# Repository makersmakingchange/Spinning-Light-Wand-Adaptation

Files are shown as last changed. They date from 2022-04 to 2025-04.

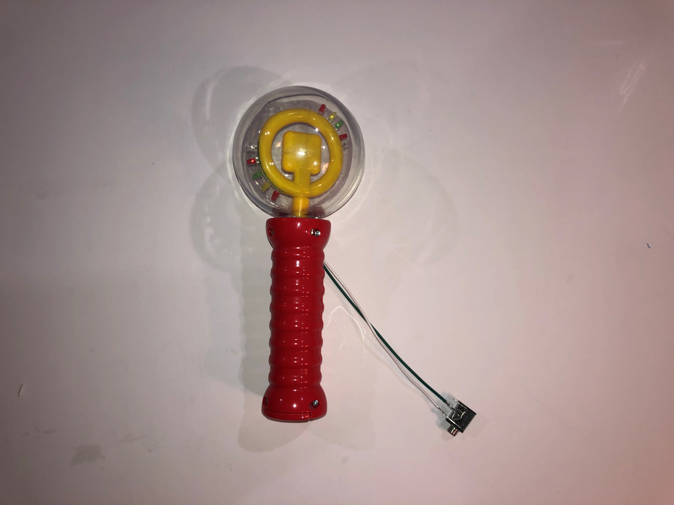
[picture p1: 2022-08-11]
Photos/solder the monojack.jpg

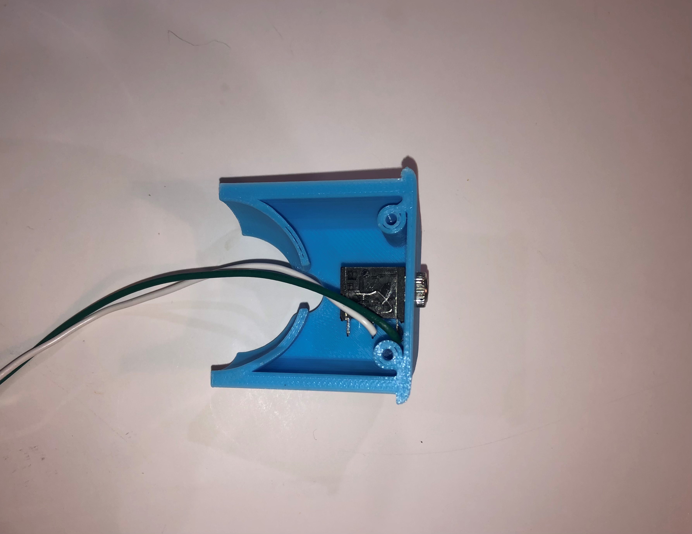
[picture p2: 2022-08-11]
Photos/mono jack.jpg

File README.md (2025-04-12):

# Spinning Light Wand Adaptation
The Spinning Light Wand Adaptation comprises instructions and files to adapt a commercially available Spinning Light Wand toy for use with an assistive switch. The toy is modified so that it has a 3.5 mm jack in place of the button. When a standard assistive switch with a 3.5 mm mono jack is attached and activated, the toy will activate. The toy is mounted into a 3D printed base that keeps the toy upright and houses the input jack. 

A switch-adapted Spinning Light Wand mounted in a blue 3d-printed base.

## More info at
- Makers Making Change Project Page: https://makersmakingchange.com/project/spinning-light-wand-toy-adaptation/
- Vancouver Hack Space Forum Thread: https://talk.vanhack.ca/t/adapting-toy-wands-for-mmc

## Getting Started

### 1. Order the Off-The-Shelf Components

The [Bill of Materials](/Documentation/Working_Documents/Spinning_Light_Wand_BOM_V1.1.xlsx) lists all of the parts and components required to adapt the Spinning Light Wand. The toy is typically available at Walmart stores.

### 2. Print the 3D Printable components
Print the components. All of the files and individual print files can be in the [Build_Files](Build_Files) folder.

### 3. Assembly
Reference the [Assembly Guide v1.0](/Documentation/Spinning_Light_Wand_Assembly_Guide_V1.0.pdf) or [Assembly Guide v1.1](/Documentation/Spinning_Light_Wand_Assembly_Guide_V1.1.pdf) for the tools and steps required to build each portion.

## Files
### Documentation
| Document             | Version | Link |
|----------------------|---------|------|
| Design Rationale     | 1.1     | [Spinning_Light_WandDesign_Rationale](/Documentation/Spinning_Light_Wand_Design_Rationale.pdf)     |
| Bill of Materials    | 1.1     | [Spinning_Light_Wand_Bill_of_Materials](/Documentation/Working_Documents/Spinning_Light_Wand_BOM_V1.1.xlsx)     |
| 3D Printing Guide    | 1.1     | [Spinning_Light_Wand_3D_Printing_Guide](/Documentation/Spinning_Light_Wand_3D_Printing_Guide.pdf)     |
| Assembly Guide       | 1.0     | [Spinning_Light_Wand_Assembly_Guide](/Documentation/Spinning_Light_Wand_Assembly_Guide_V1.0.pdf)     |
| Assembly Guide       | 1.1     | [Spinning_Light_Wand_Assembly_Guide](/Documentation/Spinning_Light_Wand_Assembly_Guide_V1.1.pdf)     |
| Maker Checklist      | 1.1     | [Spinning_Light_Wand_Maker_Checklist](/Documentation/Spinning_Light_Wand_Checklist.pdf)     |
| User Guide           | 1.0     | [Spinning_Light_Wand_User_Guide](/Documentation/Spinning_Light_Wand_User_Guide_V1.0.pdf)    |
| User Guide           | 1.1     | [Spinning_Light_Wand_User_Guide](/Documentation/Spinning_Light_Wand_User_Guide_V1.1.pdf)    |
| Changelog            | 1.1     | [Spinning_Light_Wand_Changelog](/Documentation/Spinning_Light_Wand_Changelog.pdf)     |

### Design Files
- [CAD Files](/Design_Files)

### Build Files
 - [3D Printing Files](/Build_Files)

## Attribution
This adaptation was designed by Mimi Xia of the [Makers Making Change Vancouver Chapter](https://vanhack.ca/wp/makers-making-change-vancouver-chapter/). 

3D Printed Wand Base v1.0 designed by Mimi Xia.

3D Printed Wand Base v1.1 designed by Jake McIvor – Makers Making Change.

Neil Squire / Makers Making Change assisted with the creation of the documentation.

## License
Everything needed or used to design, make, test, or prepare the Spinning Light Wand Adaptation is licensed under the CERN 2.0 Permissive license https://ohwr.org/project/cernohl/wikis/Documents/CERN-OHL-version-2 (CERN-OHL-P) .

Accompanying material such as instruction manuals, videos, and other copyrightable works that are useful but not necessary to design, make, test, or prepare the Spinning Light Wand Adaptation are published under a Creative Commons Attribution-NonCommercial-ShareAlike 4.0 license https://creativecommons.org/licenses/by-nc-sa/4.0/ (CC BY-NC-SA 4.0)

----

<!-- ABOUT MMC START -->
## About Makers Making Change
[Makers Making Change Logo](https://www.makersmakingchange.com/)

Makers Making Change is a program of [Neil Squire](https://www.neilsquire.ca/), a Canadian non-profit that uses technology, knowledge, and passion to empower people with disabilities.

Makers Making Change leverages the capacity of community based Makers, Disability Professionals and Volunteers to develop and deliver affordable Open Source Assistive Technologies.

 - Website: [www.MakersMakingChange.com](https://www.makersmakingchange.com/)
 - GitHub: [makersmakingchange](https://github.com/makersmakingchange)
 - Bluesky: [@makersmakingchange.bsky.social](https://bsky.app/profile/makersmakingchange.bsky.social)
 - Instagram: [@makersmakingchange](https://www.instagram.com/makersmakingchange)
 - Facebook: [makersmakechange](https://www.facebook.com/makersmakechange)
 - LinkedIn: [Neil Squire Society](https://www.linkedin.com/company/neil-squire-society/)
 - Thingiverse: [makersmakingchange](https://www.thingiverse.com/makersmakingchange/about)
 - Printables: [MakersMakingChange](https://www.printables.com/@MakersMakingChange)

### Contact Us
For technical questions, to get involved, or to share your experience we encourage you to [visit our website](https://www.makersmakingchange.com/) or [contact us](https://www.makersmakingchange.com/s/contact).
<!-- ABOUT MMC END -->

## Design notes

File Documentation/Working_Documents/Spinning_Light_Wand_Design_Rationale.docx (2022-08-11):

# Introduction

The toy should be activatable by connecting a standard assistive switch equipped with a 3.5 mm mono plug. This adaptation is intended for users that may have difficulty holding the toy and/or activating the small button independently.

# Requirements

## Goals

G01 | Make the toy more accessible by adding the ability to use an assistive switch.

## Functional Requirements

F01 | Must have a female 3.5 mm jack connected such that when tip and sleeve contacts are closed the toy activates.

## Non-functional Requirement

NF01

## Constraints

C01 | Adaptation should be suitable for a volunteer maker to complete.
C02 | Adaptation should require simple hand tools; screwdrivers, soldering iron

# Ideation

This toy has also been switch adapted by using a battery interrupter and using tape or a strap to fix the built-in button in the on position. A custom 3d printed collar could also be used to keep the built-in button depressed. This requires no permanent modification to the toy.

## Possible Alternatives

The following toys are a similar style but may have a different size or wiring.

### Rhode Island Novelty Light-up Magic Ball Wand, One Piece

- https://www.amazon.ca/Rhode-Island-Novelty-Magic-Flashing/dp/B009A6PIVG
- $ 16 CAD

### ArtCreativity Light up Orbiter Spinning Wand | 7â€� LED Electronic Spin Toy for Kids with Batteries Included | Great Gift Idea for Boys Girls Toddlers | Fun Birthday Party Favor/ Carnival Prize

- https://www.amazon.ca/ArtCreativity-Spinning-Electronic-Batteries-Included/dp/B07D7GQFMZ
- $20 CAD

### ArtCreativity 7.5 Inch Light Up Magic Ball Toy Wand for Kids - Flashing LED Wand for Boys and Girls - Thrilling Spinning Light Show - Batteries Included - Fun Gift or Birthday Party Favor

- https://www.amazon.ca/ArtCreativity-Inch-Light-Magic-Ball/dp/B07RG7DDW6
- $32 CAD

### Spinning Light-Up Wand for Kids in Gift Box, Rotating LED Toy Wand for Boys and Girls, Magic Princess Sensory Toys for Autistic Children, Best Birthday Gift for Kids 3, 4, 5, 6, 7

- https://www.amazon.ca/Spinning-Light-Up-Rotating-Princess-Autistic/dp/B082VFSJZP
- $43 CAD

# Prototyping

Several versions of the base were 3D printed and iterations and improvements were made accordingly. The 3D printed wand stand v1.0 was strudy but overall changes were made to decrease the print time of the device, as well as eliminate the need for supports. Some people suggested that it is rather difficult to get all of the supports off.

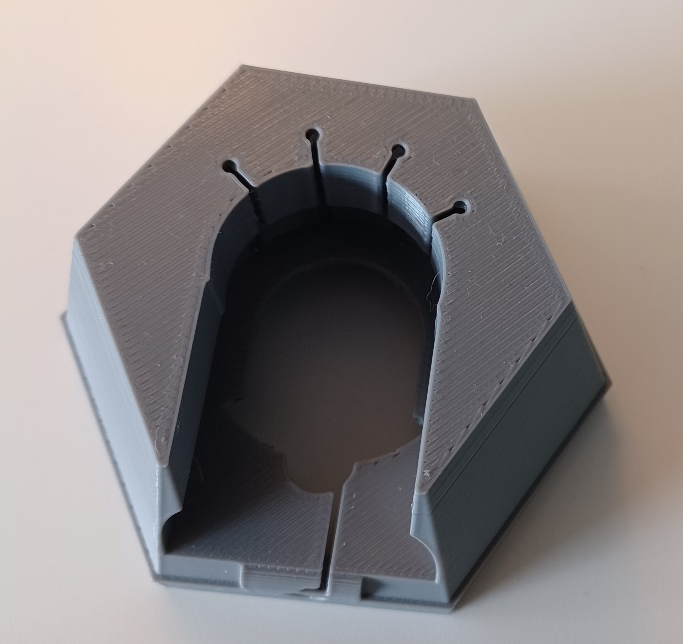
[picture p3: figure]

The Spinning Wand 3D Printed Stand v1.1 was developed as it requires no print supports, and has a quicker print time. Between iterations of this version of the wand stand, the following changes were made:

- Optimizing the hole in the base so that the battery cover could be removed in the event that the batteries need to be changed.
- Optimizing the clearance between the two 3D printed pieces so they were easy to slide together.

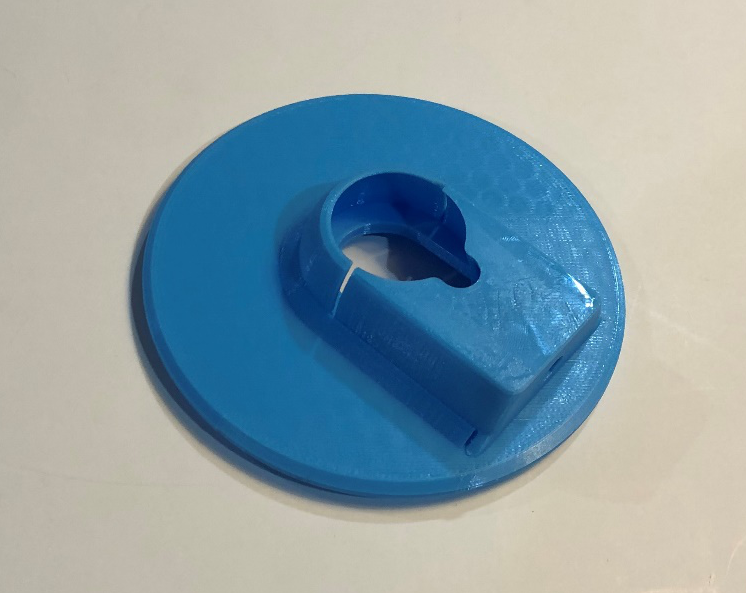
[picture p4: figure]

# Testing

The adapted toy has been tested by plugging in a switch into the 3.5mm jack located in the 3D printed base.

# Detailed Design – V1.1

## Spinning Light Wand Toy

The spinning wand toy used for this toy adaption was purchased at Walmart for $5.

- SKU 6000201173988
- https://www.walmart.ca/en/ip/spinning-light-wand-yellowblue/6000201173987

## 3D Printed Base

The 3D printed base was optimized to significantly reduce the print time, as well as eliminate the need for printing with supports. The supports on the first version of the device could be very challenging to remove, so there was a need to redesign the base. This was achieved by printing the base in 2 parts. As shown below, the smaller piece slides into the base to enclose the wand base between them. The mono jack sits in the circular hole. There are two small screw holes in each piece that align hold the two halves together. The bell-shaped hole in the 3D printed base is used to open the battery compartment on the wand without having to disassemble the 3D printed base.

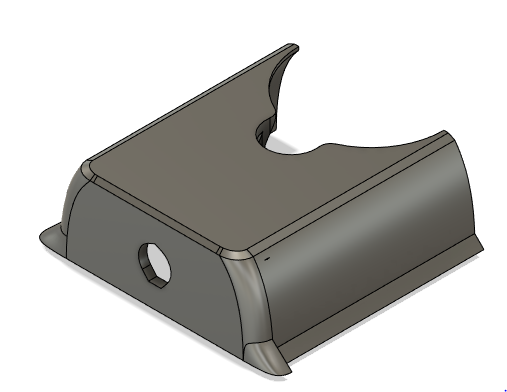
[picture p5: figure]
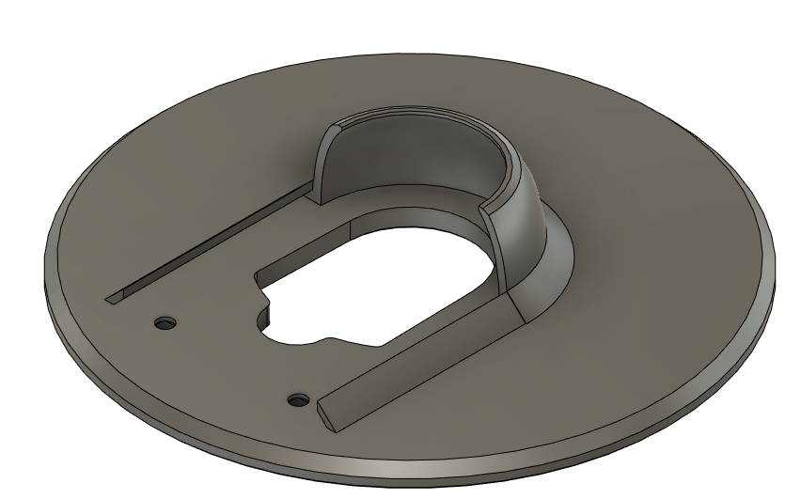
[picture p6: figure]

# Opportunities for Improvement

- Investigate options for putting external switch jack in parallel with built-in switch so that toy can be activated using either option
- The toy still slightly vibrates even with the non-slip circles. Further improvements are required to prevent the toy from moving.

© 2022 by Neil Squire / Makers Making Change. This work is licensed under the CC BY NC SA 4.0 License: http://creativecommons.org/licenses/by-nc-sa/4.0 Files available at https://makersmakingchange.com/project/spinning-light-wand-toy-adaptation/ Page 1 of 1

V1.1 | JUNE 2022 Spinning Light Wand Toy Adaptation Design Rationale

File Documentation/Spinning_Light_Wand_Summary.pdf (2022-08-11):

V1.1 | JUNE 2022

## Spinning Light Wand Toy Adaptation

## SUMMARY

© 2022 by Mimi Xia.
This work is licensed under the CC BY NC SA 4.0 License: http://creativecommons.org/licenses/by-nc-sa/4.0
Files available at https://makersmakingchange.com/project/spinning-light-wand-toy-adaptation/ (https://makersmakingchange.com/?post_type=project&p=14500&preview=true) | Page 1 of

### Title

Spinning Light Wand Toy Adaptation

### Subtitle

A switch adapted toy with spinning lights.

### Overview

The Spinning Light Wand Adaptation comprises instructions and files to adapt a commercially available Spinning Light Wand toy for use with an assistive switch. The toy is modified so that it has a 3.5 mm jack in place of the button.

### Usage

Connect an assistive switch with a 3.5 mm mono plug to the 3.5 mm mono jack on the base of the adapted toy. When the assistive switch is activated, the lights will turn on and spin within the plastic globe. The spinning wand stands in a 3D printed base. There are two versions of this base available for request: v1.0, and v1.1. Please specify to the maker which version you would like.

Cost
The cost of materials for this project is approximately $10-$15 CAD. This does not include the cost of component shipping.

Build Instructions
The necessary files and information required to switch adapt the toy switch are available in the linked GitHub repository or via the downloadable Zip file. The build consists of a commercially available toy, some 3D printed components, and some electronic components. Refer to the Spinning Light Wand Adaptation Assembly Guide.

Skills Required
- 3D Printing
- Soldering
- Mechanics

Time Required
Version 1.1:
- 3D Printing: ~3 hr
- Assembly: ~1 hr

Version 1.0:

- 3D Printing: ~6 hr

## SUMMARY

Files available at https://makersmakingchange.com/project/spinning-light-wand-toy-adaptation/ (https://makersmakingchange.com/?post_type=project&p=14500&preview=true) | Page 2 of
- Assembly: ~1 hr

Tools/Materials
Version 1.1:
- #0 Phillips Screwdriver
- #0 Robertson Screwdriver (depending on which screws you got)
- Soldering Iron & Solder
- Hot Glue Gun & Hot Glue sticks

Version 1.0:

- #0 Phillips Screwdriver
- Flat head screwdriver
- Soldering Iron & Solder
- Hot Glue Gun & Hot Glue sticks
- Super Glue

Components
Refer to the Bill of Materials.

Version 1.1:

- 1x Spinning Light Wand Toy
- 1x 3.5 m Mono Jack
- 2x 30cm pieces of wire
- 2x #4 1/2" screws
- 4x Nonslip Circles

Version 1.0:

- 1x Spinning Light Wand Toy
- 1x 3.5 m Mono Jack
- 2x 20cm pieces of wire

3D Printing
Refer to the Spinning Light Wand Adaptation 3D Printing Guide.

Version 1.1:

- 1x Wand Base
- 1x Jack Cover

Version 1.0:

## SUMMARY

Files available at https://makersmakingchange.com/project/spinning-light-wand-toy-adaptation/ (https://makersmakingchange.com/?post_type=project&p=14500&preview=true) | Page 3 of
- 1x Wand Base
- 1x Bottom Cover

### Attribution

This adaptation was designed by Mimi Xia of the [Makers Making Change Vancouver Chapter] (https://vanhack.ca/wp/makers-making-change-vancouver-chapter/) under the CC BY-SA 4.0 license.

3D Printed Wand Base v1.0 designed by Mimi Xia under the CC BY-SA 4.0 license.

3D Printed Wand Base v1.1 designed by Jake McIvor – Makers Making Change under the CC BY-SA 4.0 license.

Neil Squire / Makers Making Change assisted with the creation of the documentation that is under the CC BY-SA 4.0 license.

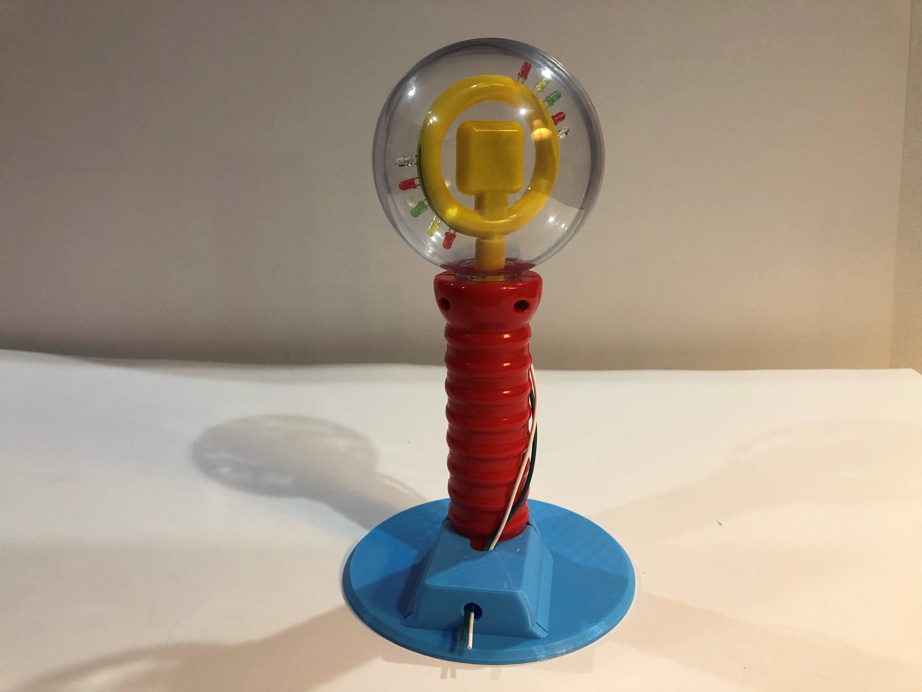
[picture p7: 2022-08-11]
Photos/feed wires through base.jpg

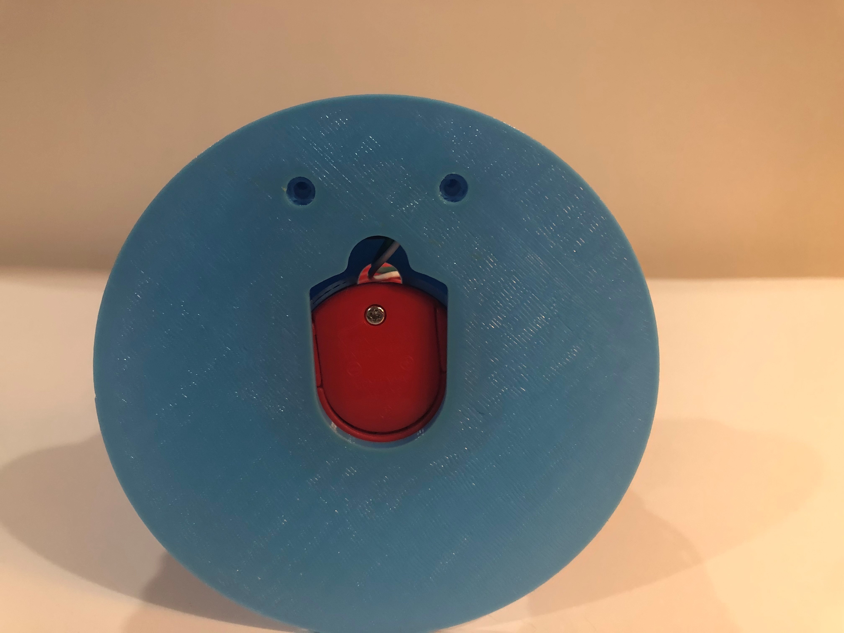
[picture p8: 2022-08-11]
Photos/battery cover.jpg

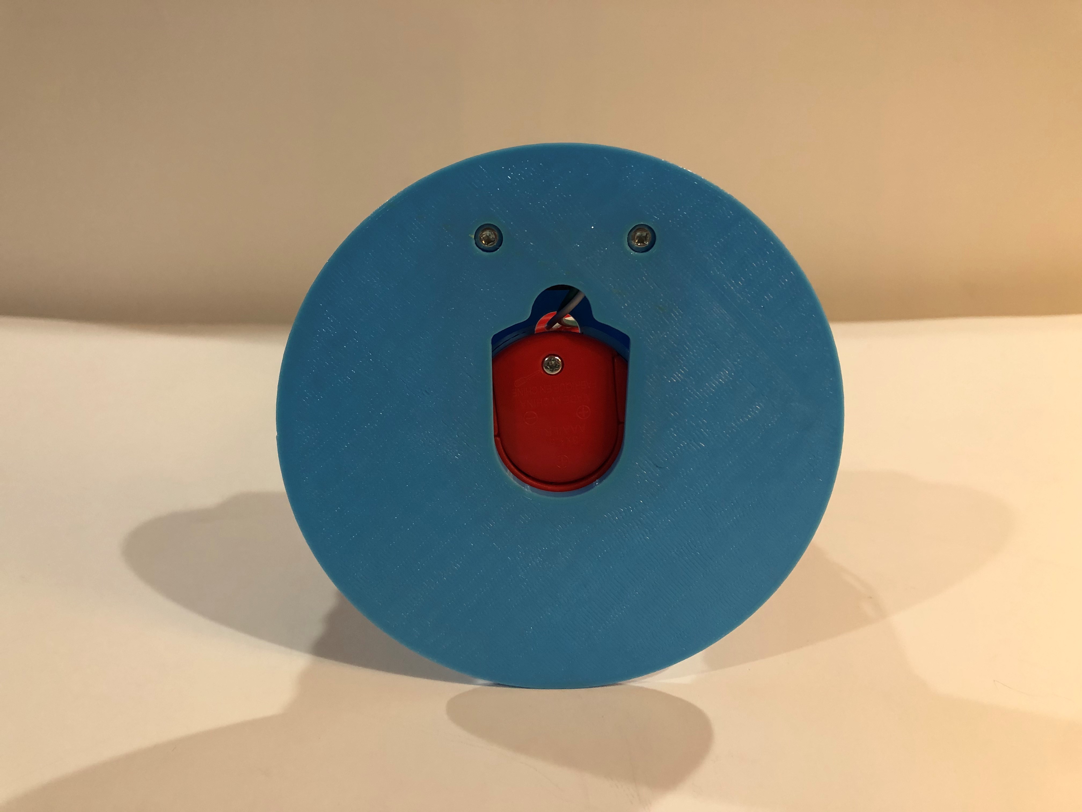
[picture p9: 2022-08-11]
Photos/align holes.jpg

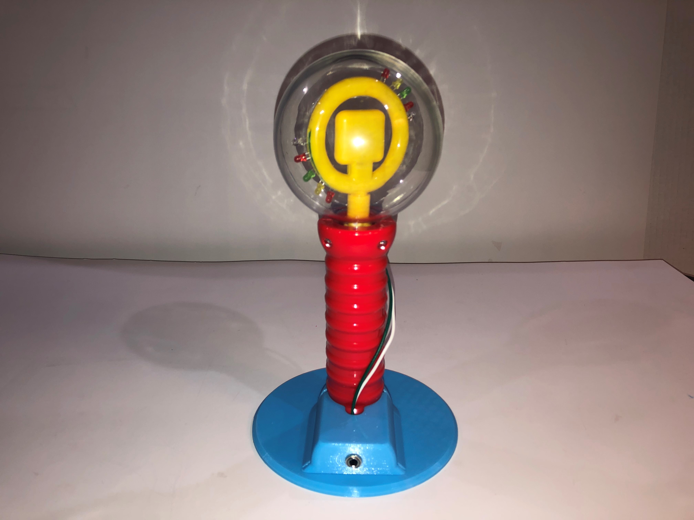
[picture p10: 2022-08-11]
Photos/in base.jpg

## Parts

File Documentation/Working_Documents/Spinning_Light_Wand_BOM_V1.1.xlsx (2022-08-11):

 | Spinning Light Wand Adaptation |  | Total Cost | Total Print time (hr) | Total filament (g)
 | Version: V1.1 (V1.0 BOM found below) | June, 2022 | $9.12 | 2.58 | 37
ID | Commercial Parts
 |  | Model | QTY | Pkg Quantity | Price per package | Price per Unit | Price for qty needed | Link
1 | Spinning Light Wand Toy | SKU 6000201173988 | 1 | 1 | $5.00 | $5.00 | $5.00 | https://www.walmart.ca/en/ip/spinning-light-wand-yellowblue/6000201173987
2 | 3.5 mm Mono Jack | Shurter 4832.2211 | 1 | 1 | $2.02 | $2.02 | $2.02 | https://www.digikey.ca/en/products/detail/schurter-inc/4832-2211/2646631
3 | #4 1/2" screws | 9018940 | 8 | 75 | $8.22 | $0.11 | $0.88 | https://www.amazon.ca/Prime-Line-9018940-Self-Tapping-Phillips-Plated/dp/B074ZXK788?rnid=12035759011
4 | Non-slip circles |  | 4 | 20 | $1.50 | $0.07 | $0.30 | Bought at dollarama
 | 3D Printed Parts ESTIMATED PRICING USING 1 KG ROLL COST: | $25.00
 | Part |  | QTY | TOTAL Mass (g) | Estimated Price | Print Time (Min) | Link
5 | Base | Base.stl | 1 | 29 | $0.73 | 112
6 | Jack Cover | Jack_Cover.stl | 1 | 8 | $0.20 | 43
 |  |  |  | Total Print Cost: | $0.93
 | Tools for Assembly
 | #0 Phillips Screwdriver
 | #0 Robertson Screwdriver (depending on which screws you get)
 | Soldering Iron
 | Hot glue gun
 | Alternatives (if there are other sources for some parts link them below)
 | Part and description | Link
 | 3.5 mm Mono Jack | https://www.digikey.ca/en/products/detail/cui-devices/SJ1-3513/738683
 | Can likely buy screws in smaller quanities at local hardware store. They typically have a #0 Robertson head
 |  |  | Total Cost | Total Print time (hr) | Total filament (g)
 | Version: V1.0 |  | $9.73 | 6.13 | 62
 | Commercial Parts
 |  | Model | QTY | Pkg Quantity | Price per package | Price per Unit | Price for qty needed | Link
 | Spinning Light Wand Toy | SKU 6000201173988 | 1 | 1 | $5.00 | $5.00 | $5.00 | https://www.walmart.ca/en/ip/spinning-light-wand-yellowblue/6000201173987
 | 3.5 mm Mono Jack | Shurter 4832.2211 | 1 | 1 | $2.02 | $2.02 | $2.02 | https://www.digikey.ca/en/products/detail/schurter-inc/4832-2211/2646631
 | 1/2" Hex Nuts |  | 2 | 1 | $0.58 | $0.58 | $1.16 | https://www.homedepot.ca/product/paulin-1-2-13-inch-finished-hex-nut-zinc-plated-grade-5-unc/1000123718
 | 3D Printed Parts ESTIMATED PRICING USING 1 KG ROLL COST: | $25.00
 | Part |  | QTY | TOTAL Mass (g) | Estimated Price | Print Time (Min) | Link
 | Base | Base.stl | 1 | 53 | $1.32 | 320
 | Base Bottom Cover | Base_Bottom_Cover.stl | 1 | 9 | $0.22 | 48
 |  |  |  | Total Print Cost: | $1.55
 | Tools for Assembly
 | #0 Phillips Screwdriver
 | Flat head screw driver
 | Soldering Iron
 | Hot glue gun
 | Super Glue
 | Alternatives (if there are other sources for some parts link them below)
 | Part and description | Link
 | 3.5 mm Mono Jack | https://www.digikey.ca/en/products/detail/cui-devices/SJ1-3513/738683

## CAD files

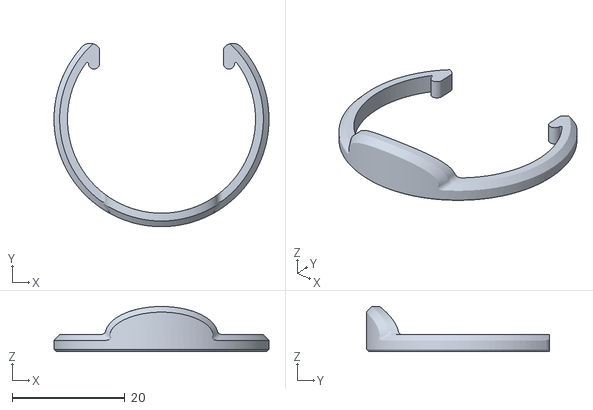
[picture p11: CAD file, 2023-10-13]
Build_Files/Light_Wand_Button_Clamp_for_Battery_Interruptor.stl
38.2 x 32.6 x 8.00

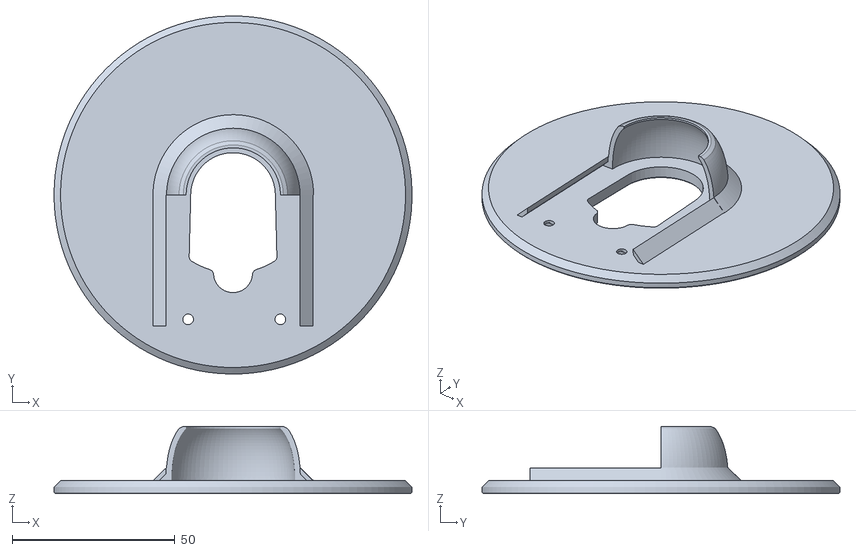
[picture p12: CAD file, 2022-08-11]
Build_Files/V1.1/Base.stl
110.0 x 110.0 x 20.6

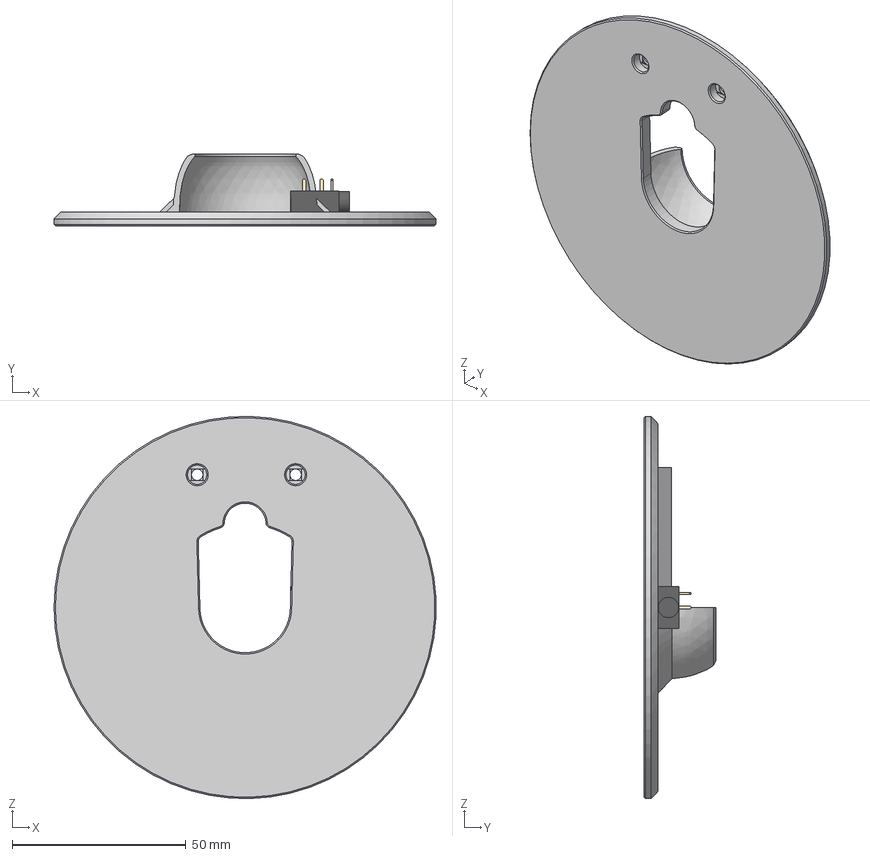
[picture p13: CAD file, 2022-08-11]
Design_Files/V1.1/Spinning Light Wand Stand.step
109.9 x 20.6 x 110.0 mm
Switch_Jack
Base

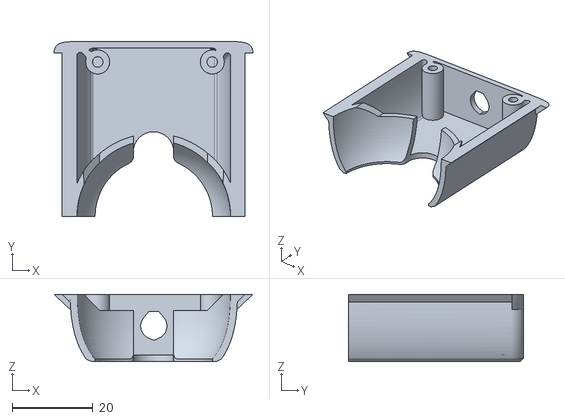
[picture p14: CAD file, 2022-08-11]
Build_Files/V1.1/Jack_Cover.stl
49.2 x 43.3 x 16.6

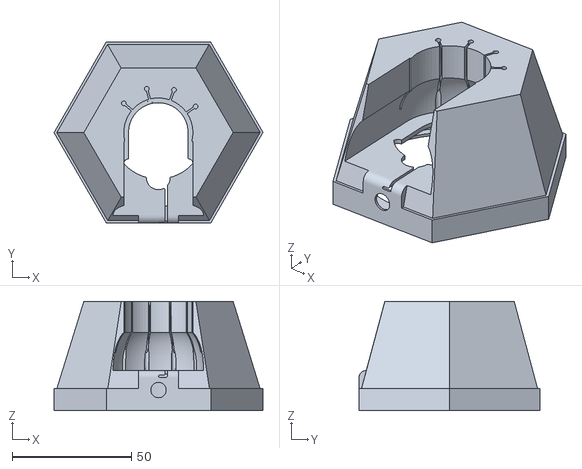
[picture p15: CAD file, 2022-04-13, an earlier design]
Build_Files/V1.0/Base.stl
87.8 x 76.1 x 45.9

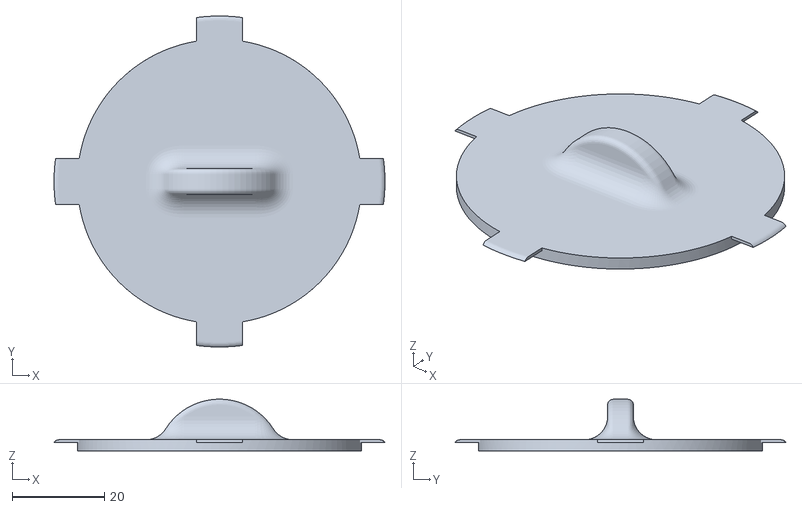
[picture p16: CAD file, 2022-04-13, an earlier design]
Build_Files/V1.0/Base_Bottom_Cover.stl
71.8 x 71.8 x 11.2

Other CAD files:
Design_Files/V1.0/Spinning_Light_Wand_Adaptation.f3d
Design_Files/V1.1/Spinning Light Wand Stand.3mf
Design_Files/V1.1/Spinning_Wand_Base_v1.1.f3z

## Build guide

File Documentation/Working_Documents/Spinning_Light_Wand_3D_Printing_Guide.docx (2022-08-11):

# 3D Printing Summary

Metrics | V 1.1 | V 1.0
Total Print Time (hr:min) | 2:35 | 6:08
Total Number of Components | 2 | 2
Typical Total Mass (g) | 37 | 62
Typical Number of Print Setups | 1 | 1

# 3D Printing Settings

This design is intended to be printed with a 0.4 mm nozzle.

Version | Print File Name | Qty | Total Print Time (hr:min) | Mass (g) | Infill (%) | Support (Y/N) | Layer Height (mm) | Notes
V1.1 | Base.stl | 1 | 1:52 | 29 | 20 | N | 0.2 | Print in the orientation given in the stl file.
V 1.1 | Jack_Cover.stl | 1 | 0:43 | 8 | 20 | N | 0.2 | Print in the orientation given in the stl file.
V 1.0 | Base.stl | 1 | 5:20 | 53 | 20 | Y | 0.2 | Support on build plate only.
V 1.0 | Base_Bottom_Cover.stl | 1 | 0:48 | 9 | 20 | Y | 0.2 | Support on build plate only.

Version | Length (mm) | Width (mm) | Height (mm)
V 1.1 | 114 | 114 | 18
V 1.0 | 88 | 76 | 46

# Post-Processing

V1.0: Carefully remove supports from Base and Base Bottom Cover.

V1.1: The Spinning Light Wand Base and Jack Cover are printed without supports; hence no post-processing is required.

# Customization Options

The user can request which version of the 3D printed base they would like (V1.0 or V1.1). The user can also request that the device be printed in multiple colours.

# Examples of Quality Prints

Below is a picture of what quality is expected from printing these devices.

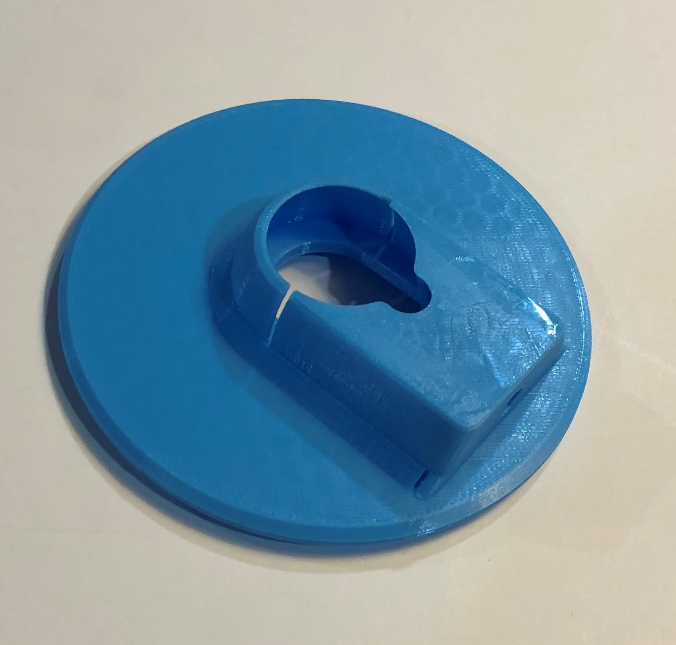
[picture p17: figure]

Version 1.1 | Version 1.0

© 2022 by Neil Squire / Makers Making Change. This work is licensed under the CC BY NC SA 4.0 License: http://creativecommons.org/licenses/by-nc-sa/4.0 Files available at https://makersmakingchange.com/project/spinning-light-wand-toy-adaptation/ Page 1 of 1

V1.1 | JUNE 2022 Spinning Light Wand Toy Adaptation 3D Printing Guide

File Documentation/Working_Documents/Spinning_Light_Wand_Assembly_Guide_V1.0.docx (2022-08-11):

# Required Components

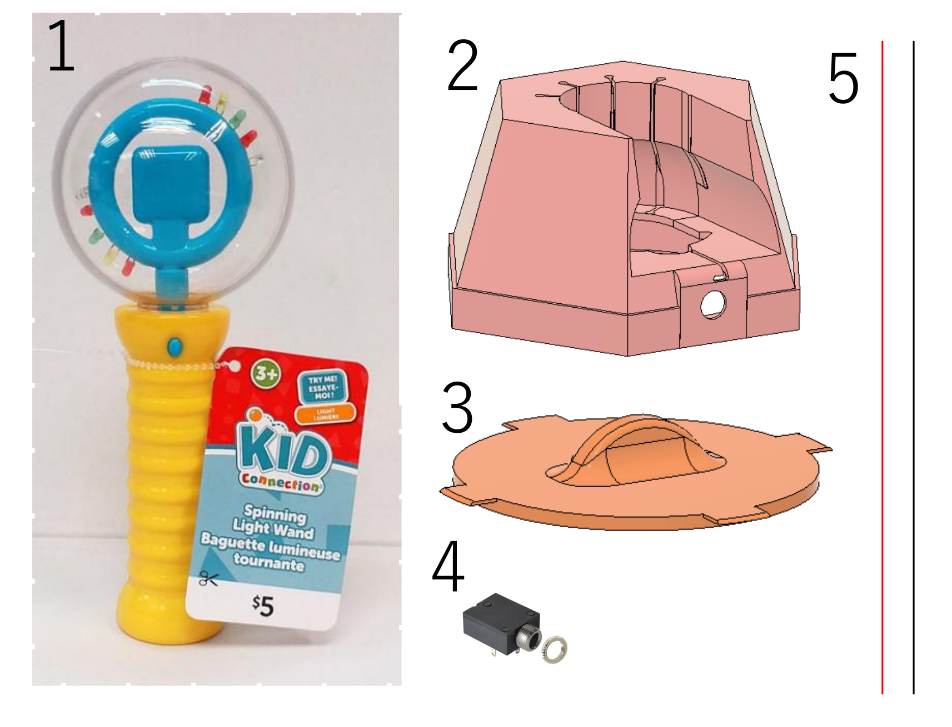
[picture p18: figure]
Diagram of components. 1: Spinning Wand Toy. 2: 3D printed base. 3: 3d printed base cover. 4: 3.5 mm mono jack. 5: 2 lengths of 20 cm long wire.

| BOM 1. Spinning Wand Toy 2. 3D Printed Base 3. 3D Printed Base Bottom Cover 4. 3.5 mm Mono jack 5. 2X 20 cm 26AWG multi-core wire or stranded wire (24-26 AWG)

# Required Tools

- #0 Phillips Screwdriver
- Flat head screwdriver
- Soldering Iron
- Hot Glue Gun
- Solder
- Hot Glue Sticks
- Super Glue

# Required Personal Protective Equipment (PPE)

- Safety Glasses

# Assembly Instructions

## Step 1

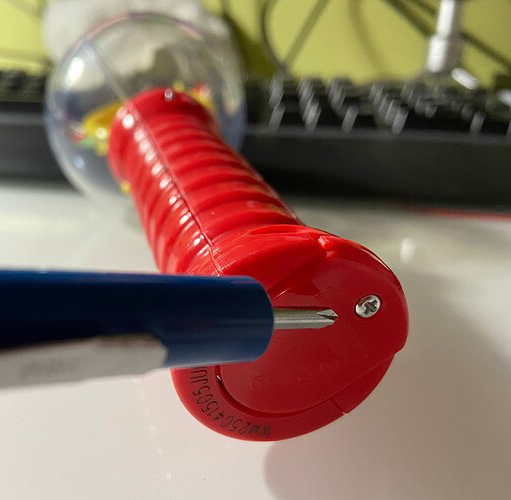
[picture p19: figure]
Picture of spinning wand showing single screw on the bottom battery cover.

Loosen the screw and remove the battery cover and batteries. CAUTION! The springs on the battery contacts may cause the batteries to be ejected forcibly.

## Step 2

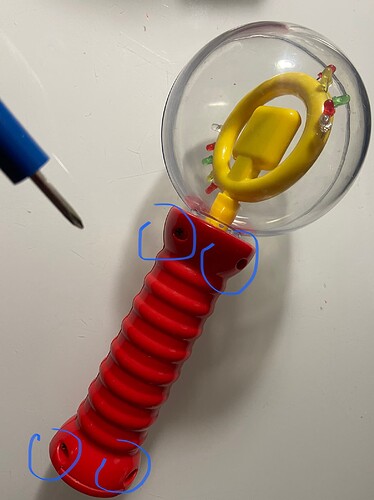
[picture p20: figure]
Picture showing location of 4 screws that hold wand handle together.

Unscrew the four (4) screws on the back of the Spinning Light Wand. Store the screws for later reassembly. CAUTION! Don’t lose the screws.

## Step 3

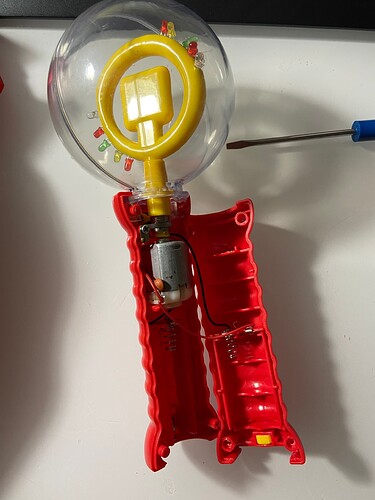
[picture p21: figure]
Picture showing wand handle separated into two halves.

Gently pry apart the two halves of the handle along the seam using a flat head screwdriver.

## Step 4

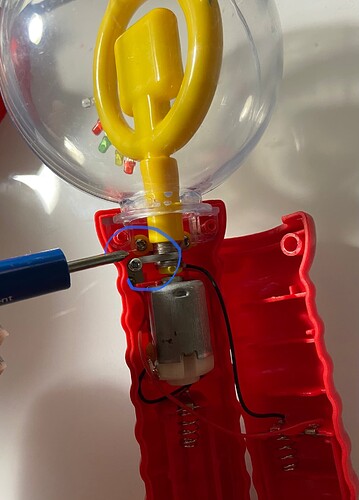
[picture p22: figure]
Picture showing location of single screw holding down metal motor contact.

Remove the screw holding the motor down, as shown in the photo, and remove the piece of metal contact. Keep the screw for later reassembly. CAUTION! Don’t lose the screw or the metal contact.

## Step 5

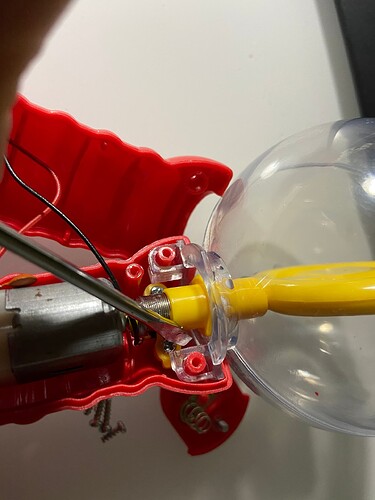
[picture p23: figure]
Picture of half of the wand showing a screwdriver being used to gently pry the clear globe off the plastic base.
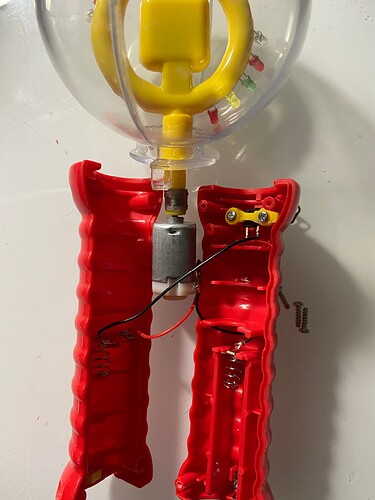
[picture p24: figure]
Picture showing the two halves of the wand separated and the globe assembly removed.

Gently pry the clear globe free from the button half of the handle The motor and the clear globe is part of the same assembly, carefully lay all the parts out, and try and avoid putting strain on any of the solder joints.

## Step 6

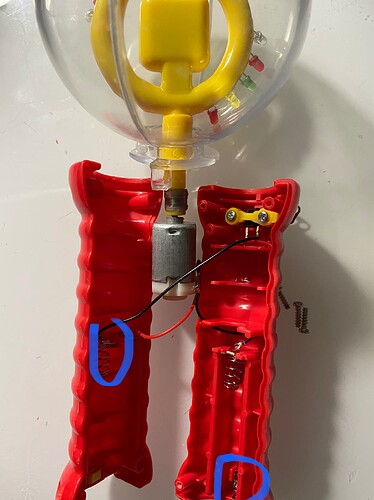
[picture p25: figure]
Picture showing the location to de-solder wires from the battery terminals. The lower terminal on the side with the button and the upper terminal on the other side.
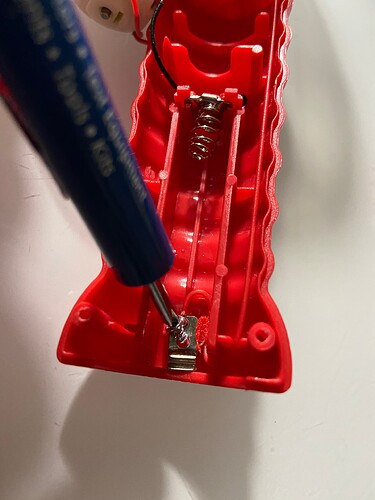
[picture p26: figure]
Picture showing the screw holding down the lower terminal on the button side being removed.

De-solder the black wire from the top of the battery holder and the red wire on the other half from the bottom of the battery holder. For the red wire, it may be easier to loosen the screw to remove the wire from under the metal clip.

## Step 7

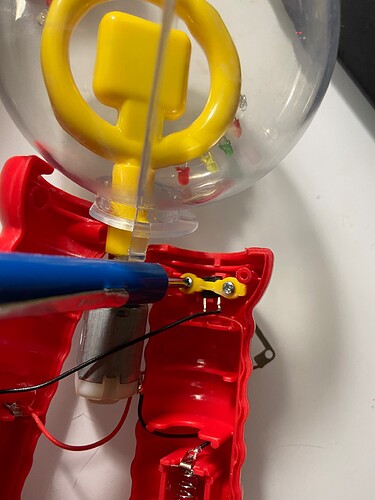
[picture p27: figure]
Picture showing the two screws that hold a plastic bar to retain the switch being removed.

Unscrew the screws attached to the yellow piece shown. Remove and discard the entire button assembly. They are no longer needed.

## Step 8

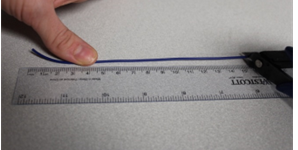
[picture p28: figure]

Cut 2 pieces of wire 30cm long. Strip approximately 1cm of the insulation from one end of each of the wires.

## Step 9

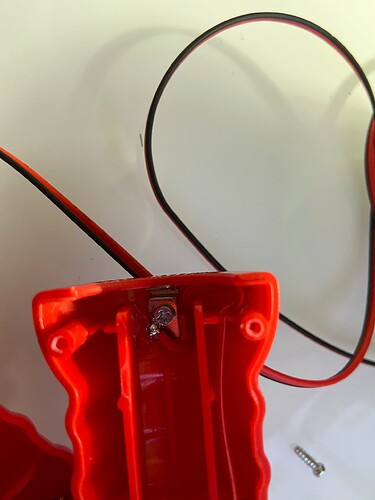
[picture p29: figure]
Picture showing the red wire soldered to the lower battery terminal on the button hole side.

Solder one of the wires to the bottom metal clip and route the wire as shown below. This is the same place where the original red wire was soldered.

## Step 10

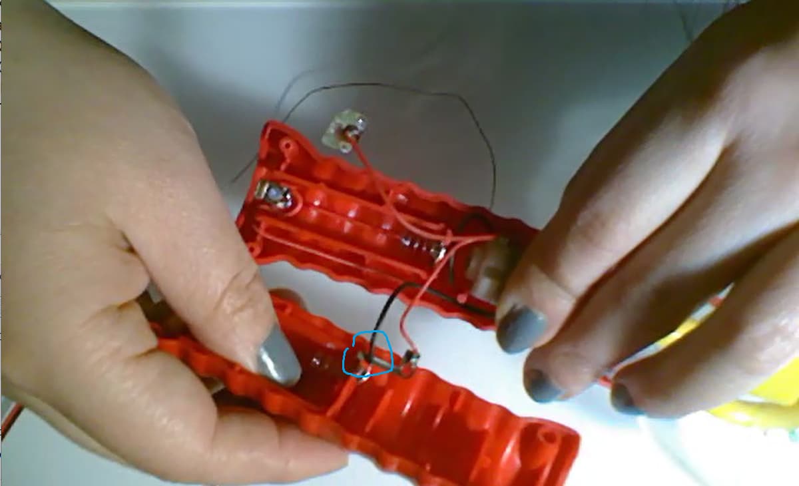
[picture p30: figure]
Picture showing black wire solder to battery terminal on non-button side.

Solder the second wire to the battery clip. This is the same place that the original black wire was desoldered from.

## Step 11

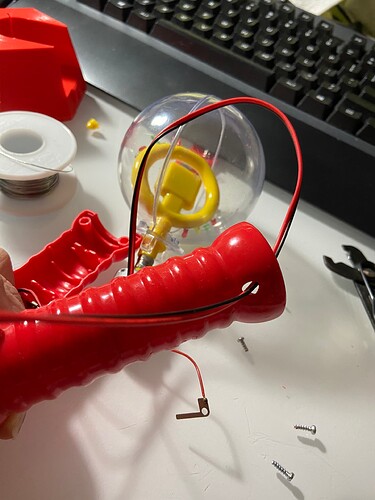
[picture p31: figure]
Picture showing the wires soldered to the battery terminals being threaded through the button hole and outside the wand.

Thread the wires through the hole that the button occupied. Avoid leaving too much slack on the wires inside as it might interfere with the moving bits.
Step 12 Route the wires through the inside of the handle as shown.

## Step 13

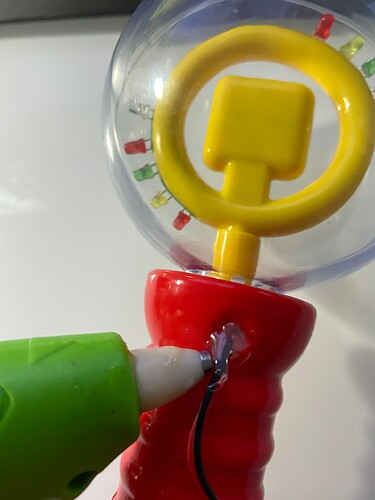
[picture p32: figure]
Picture showing hot glue gun being used to add hot glue to button hole around wires to provide strain relief.

Apply hot glue to fill up space between the wire and the hole, to add strain relief to the wire.

## Step 14

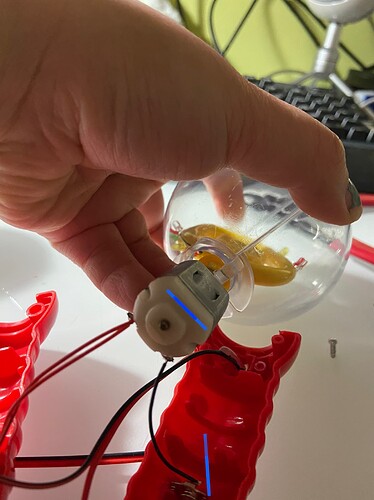
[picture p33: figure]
Photo showing globe being reinserted into wand handle. Looking down into the button-hole side of the wand, with the button-hole oriented to the top, the flat portion of motor is oriented to the left.
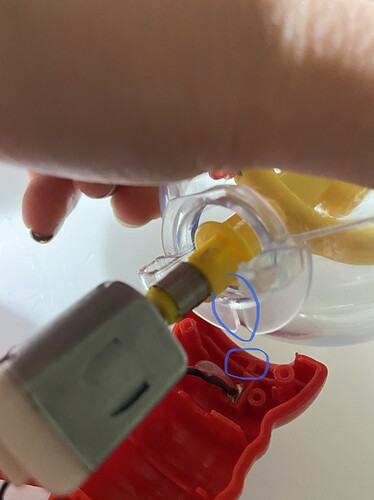
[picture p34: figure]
Photo showing globe being reinserted into non-button side of wand. A small gap in the globe portion fits into a matching portion on the wand handle.

Start reassembling the wand by putting the globe and motor assembly back into the half of the handle with the button hole. Note the alignment of the motor and the clear globe. See photos.

## Step 15

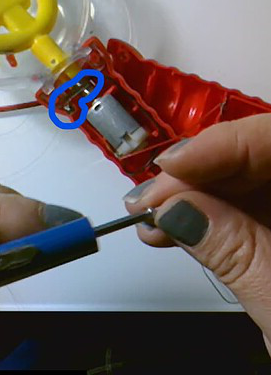
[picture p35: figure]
Photo showing L-shaped motor contact being reattached with screw into boss.

Reattach the L-shaped metal contact. Replace the screw.

## Step 16

Snap the handle closed, being careful not to pinch any wires inside. Replace all four screws. Re-insert the batteries and tighten the battery cover screw.

## Step 17

Test the switch adaptation.
Strip the other end of the wire and touch them together. If all goes well, the motor should spin and the light would come on. If not, re-open the handle and check:

- wiring: no cold solder joints or frayed/pinched wires
- mechanical interference: now wires are rubbing on the axle
- the L-shaped metal piece is making good contact against the spring on the motor axle.

## Step 18

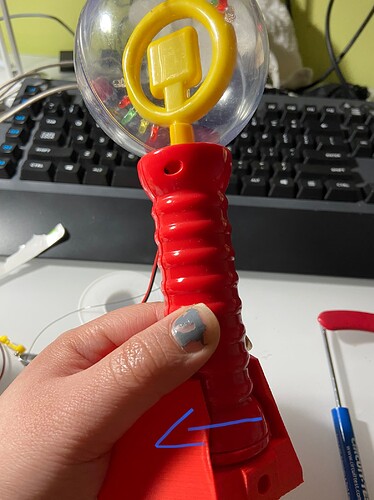
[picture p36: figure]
Photo of wand being inserted into the base. The battery cover in the wand should line up with the hole in the base.
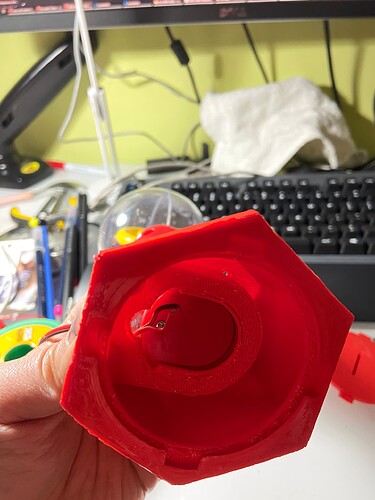
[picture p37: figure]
Photo of wand inserted into the base. The battery cover in the wand should line up with the hole in the base.

Slide the wand into the stand. Make sure the battery cover is lined up with the opening in the stand.

## Step 19

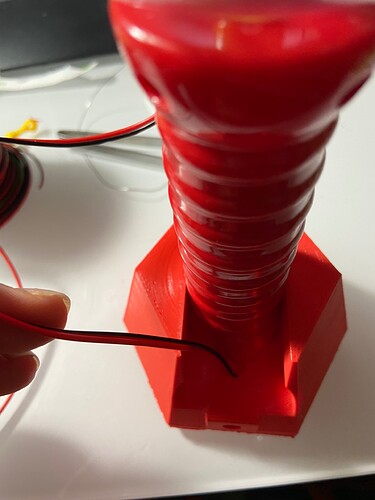
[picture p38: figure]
Picture showing the wires coming out of the button hole being routed down through the hole in the base.
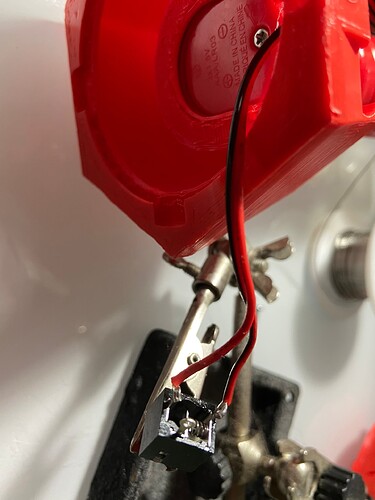
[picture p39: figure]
Picture showing the wires being soldered to the jack.

Thread the wire through the opening of the stand. Solder the wires to a mono jack as shown in photo. The wires should attach to the tip and sleeve contacts on the jack.

## Step 20

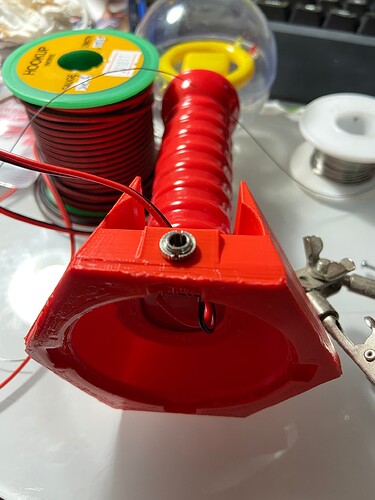
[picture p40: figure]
Picture showing the jack inserted into the base with the nut attached.

Insert the jack into the hole in the base. Thread on the nut to secure the jack in place.

## Step 21

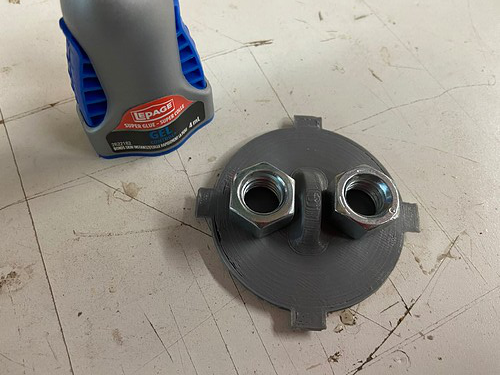
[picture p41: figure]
Picture of the base bottom cover with two nuts being superglued on either side of the coin protrusion.

Superglue something heavy like two hex nuts to the Base Bottom Cover to weigh the stand down.

## Step 22

Assemble the base bottom cover into the base.

© 2022 by Neil Squire / Makers Making Change. Photos and text by Mimi Xia. This work is licensed under the CC BY NC SA 4.0 License: http://creativecommons.org/licenses/by-nc-sa/4.0 Files available at https://makersmakingchange.com/project/spinning-light-wand-toy-adaptation/ Page 1 of 1

V1.0 | APRIL 2022 Spinning Light Wand Toy Adaptation Assembly Guide (for v1.0 Printed base)

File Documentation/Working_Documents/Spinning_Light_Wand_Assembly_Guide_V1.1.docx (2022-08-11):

# Required Components

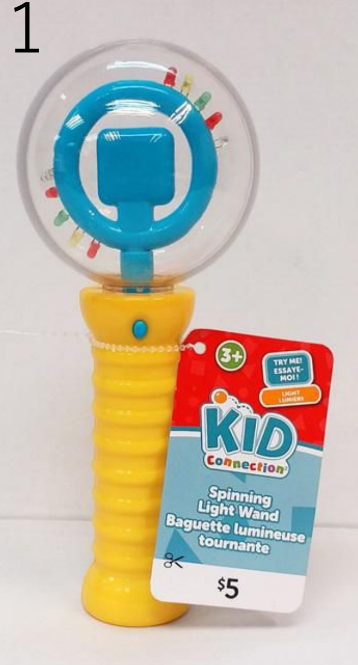
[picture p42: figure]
Diagram of components. 1: Spinning Wand Toy. 2: 3D printed base. 3: 3d printed base cover. 4: 3.5 mm mono jack. 5: 2 lengths of 20 cm long wire.

2 1 5 4 3 7 6 | BOM 1. Spinning Wand Toy 2. 3D Printed Base 3. Mono Jack Cover 4. 3.5 mm Mono jack 5. 2X 30 cm 26AWG multi-core wire or stranded wire (24-26 AWG) 6. 2x #4 1/2" screws 7. 4x nonslip circles.

# Required Tools

- #0 Phillips Screwdriver
- #0 Robertson Screwdriver (depending on what #4 screws you purchased)
- Soldering Iron and Solder
- Hot Glue Gun and Glue Sticks

# Required Personal Protective Equipment (PPE)

- Safety Glasses

# Assembly Instructions

## Step 1

Picture of spinning wand showing single screw on the bottom battery cover.

Loosen the screw and remove the battery cover and batteries. CAUTION! The springs on the battery contacts may cause the batteries to be ejected forcibly.

## Step 2

Picture showing location of 4 screws that hold wand handle together.

Unscrew the four (4) screws on the back of the Spinning Light Wand. Store the screws for later reassembly. CAUTION! Don’t lose the screws.

## Step 3

Picture showing wand handle separated into two halves.

Gently pry apart the two halves of the handle along the seam using a flat head screwdriver.

## Step 4

Picture showing location of single screw holding down metal motor contact.

Remove the screw holding the motor down, as shown in the photo, and remove the piece of metal contact. Keep the screw for later reassembly. CAUTION! Don’t lose the screw or the metal contact.

## Step 5

Picture of half of the wand showing a screwdriver being used to gently pry the clear globe off the plastic base.
Picture showing the two halves of the wand separated and the globe assembly removed.

Gently pry the clear globe free from the button half of the handle The motor and the clear globe is part of the same assembly, carefully lay all the parts out, and try and avoid putting strain on any of the solder joints.

## Step 6

Picture showing the screw holding down the lower terminal on the button side being removed.

De-solder the black wire from the top of the battery holder and the red wire on the other half from the bottom of the battery holder. For the red wire, it may be easier to loosen the screw to remove the wire from under the metal clip.

## Step 7

Picture showing the two screws that hold a plastic bar to retain the switch being removed.

Unscrew the screws attached to the yellow piece shown. Remove and discard the entire button assembly. They are no longer needed.

## Step 8


Cut 2 pieces of wire 30cm long. Strip approximately 1cm of the insulation from one end of each of the wires.

## Step 9

Picture showing the red wire soldered to the lower battery terminal on the button hole side.

Solder one of the wires to the bottom metal clip and route the wire as shown below. This is the same place where the original red wire was soldered.

## Step 10

Picture showing black wire solder to battery terminal on non-button side.

Solder the second wire to the battery clip. This is the same place that the original black wire was desoldered from.

## Step 11

Picture showing the wires soldered to the battery terminals being threaded through the button hole and outside the wand.

Thread the wires through the hole that the button occupied. Avoid leaving too much slack on the wires inside as it might interfere with the moving bits.
Step 12 Route the wires through the inside of the handle as shown.

## Step 13

Picture showing hot glue gun being used to add hot glue to button hole around wires to provide strain relief.

Apply hot glue to fill up space between the wire and the hole, to add strain relief to the wire.

## Step 14

Photo showing globe being reinserted into wand handle. Looking down into the button-hole side of the wand, with the button-hole oriented to the top, the flat portion of motor is oriented to the left.
Photo showing globe being reinserted into non-button side of wand. A small gap in the globe portion fits into a matching portion on the wand handle.

Start reassembling the wand by putting the globe and motor assembly back into the half of the handle with the button hole. Note the alignment of the motor and the clear globe. See photos.

## Step 15

Photo showing L-shaped motor contact being reattached with screw into boss.

Reattach the L-shaped metal contact. Replace the screw.

## Step 16

Snap the handle closed, being careful not to pinch any wires inside. Replace all four screws. Re-insert the batteries and tighten the battery cover screw.

## Step 17

Test the switch adaptation.
Strip the other end of the wire and touch them together. If all goes well, the motor should spin and the light would come on. If not, re-open the handle and check:

- wiring: no cold solder joints or frayed/pinched wires
- mechanical interference: now wires are rubbing on the axle
- the L-shaped metal piece is making good contact against the spring on the motor axle.

## Step 18

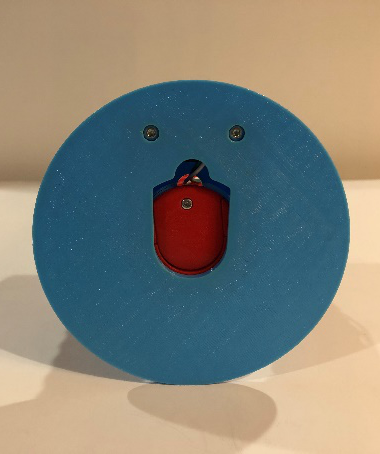
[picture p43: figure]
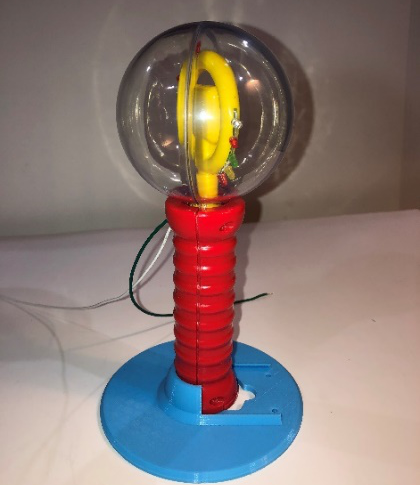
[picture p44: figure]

Slide the wand into the stand. Make sure the battery cover is lined up with the hole in the base.

## Step 19

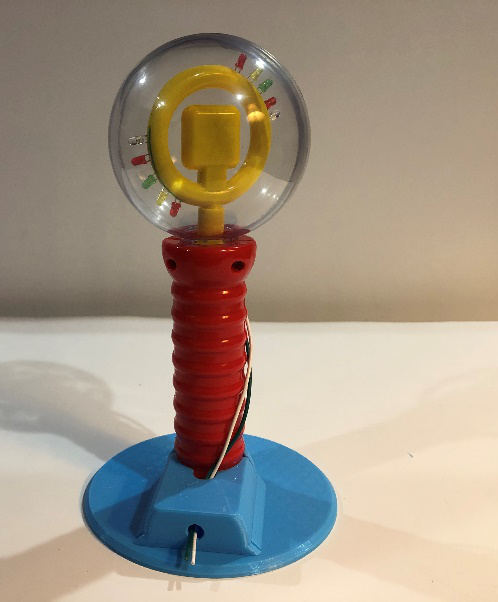
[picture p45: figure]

Slide the second pieces of the base together. While doing so, thread the wire through the opening of the stand. If the wires stick out the hole more than 1-2cm, they can be cut and striped about 1cm.

## Step 20

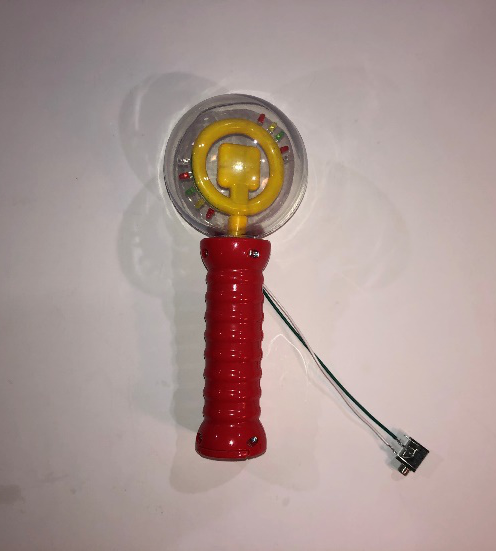
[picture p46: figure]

Remove the wand from the base. Solder the two wires to the two legs of the mono jack closest to the nut.

## Step 21

Remove the nut from the mono jack and push the mono jack through the hole. Reinstall the nut and tighten it to secure. Next, carefully bend the wires as shown.

## Step 22

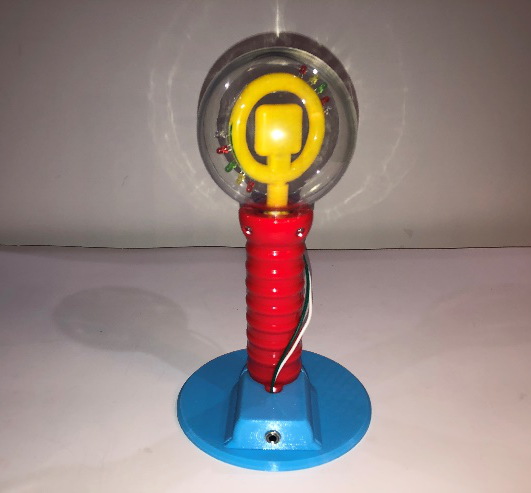
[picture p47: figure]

Slide the wand into the base again, as well as slide in the part of the base with the mono jack.

## Step 23

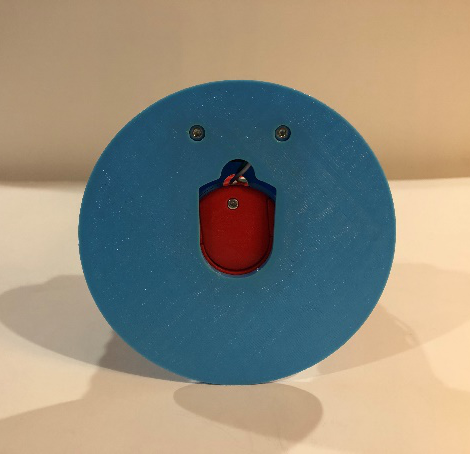
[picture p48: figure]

Set the wand on its side. Make sure the holes in the 2 3D printed parts align. Insert the two screws into the holes shown.

## Step 24

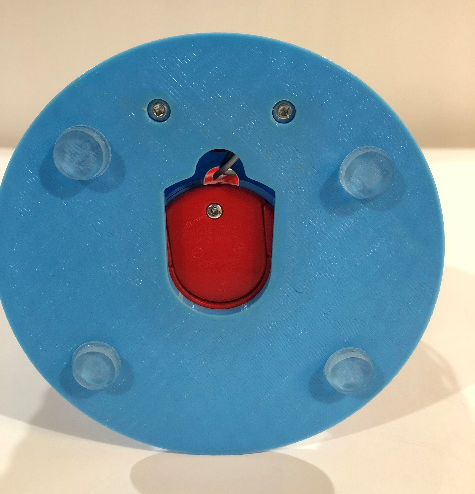
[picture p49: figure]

Attach 4 non-slip pads to the bottom of the base.

© 2022 by Neil Squire / Makers Making Change. Photos and text by Mimi Xia. This work is licensed under the CC BY NC SA 4.0 License: http://creativecommons.org/licenses/by-nc-sa/4.0 Files available at https://makersmakingchange.com/project/spinning-light-wand-toy-adaptation/ Page 1 of 1

V1.1| JUNE 2022 Spinning Light Wand Toy Adaptation Assembly Guide

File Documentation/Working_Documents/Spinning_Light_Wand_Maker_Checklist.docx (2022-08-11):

# Maker To Do List

- Read through the Assembly Guide to become familiar with required components, tools, supplies, and safety gear and overall assembly steps.
- Ask the user which 3D printed wand base they would like (Version 1.0 or Version 1.1) pictures of both can be found on the project page.
- Talk to User about customization options such as Base colour.
- Order / purchase toy.
- Order hardware components.
- Gather tools, supplies, and safety equipment.
- Adapt the toy.
- Test device.
- Print the Spinning Light Wand User Quick Guide V1.0 or V1.1 depending on which 3D printed base the user requested.

# Items to Give to User

- Assembled, adapted tested Spinning Light Wand.
- Spinning Light Wand User Quick Guide.

© 2022 by Neil Squire / Makers Making Change. This work is licensed under the CC BY NC SA 4.0 License: http://creativecommons.org/licenses/by-nc-sa/4.0 Files available at https://makersmakingchange.com/project/spinning-light-wand-toy-adaptation/ Page 1 of 1

V1.1 | JUNE 2022 Spinning Light Wand Toy Adaptation Maker Checklist

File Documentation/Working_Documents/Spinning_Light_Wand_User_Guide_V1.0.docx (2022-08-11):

## Introduction

The Switch Adapted Spinning Light Wand toy provides a way to activate and hold the toy for users who may otherwise have difficulty playing with it independently.

## Features

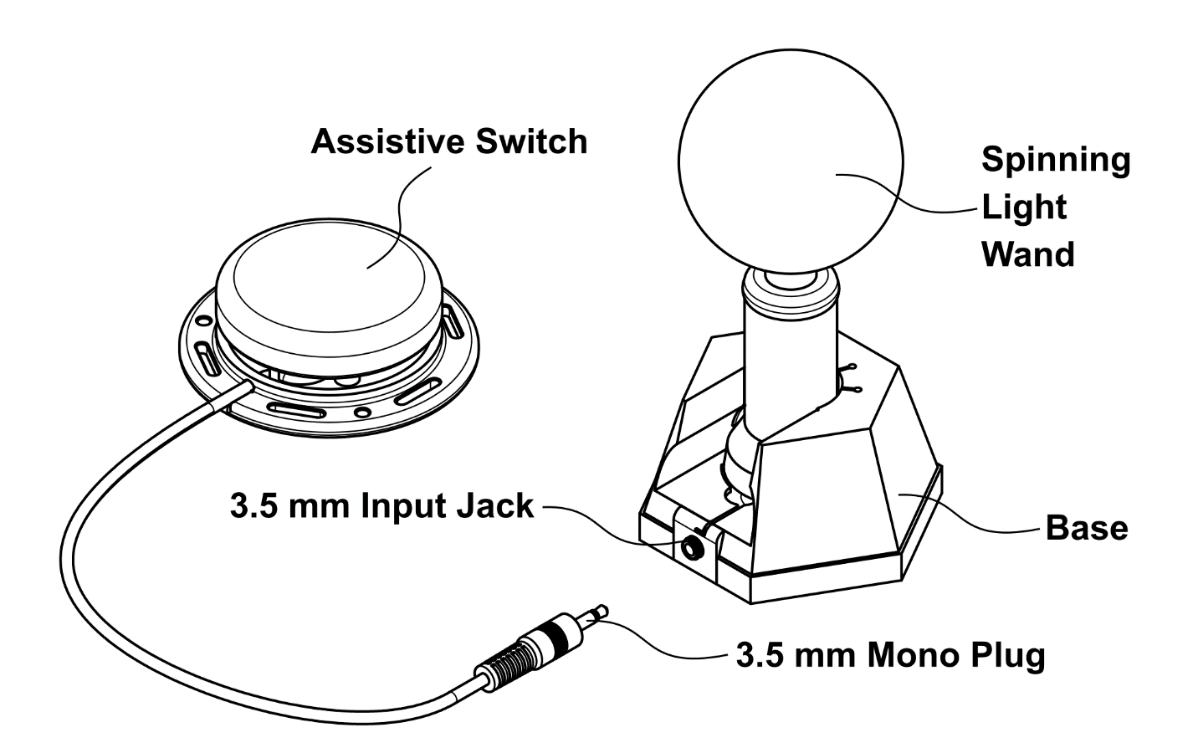
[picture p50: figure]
Diagram of the switch adapted spinning light wand. The assistive switch has a 3.5 mm mono plug. The plug is inserted into the input jack on the base to activate the toy.

## Usage

An assistive switch with a 3.5 mm mono plug is connected to the Switch input port on the Base. When the switch is activated, the lights will turn on and spin within the plastic globe.

## Compatibility

This adapted toy is compatible with assistive switches that have a 3.5 mm plug.

## Cleaning

The 3D printed base can be wiped down with a cloth. Do not submerge.

© 2022 by Mimi Xia. This work is licensed under the CC BY NC SA 4.0 License: http://creativecommons.org/licenses/by-nc-sa/4.0 Files available at https://makersmakingchange.com/project/spinning-light-wand-toy-adaptation/ Page 1 of 2

V1.0 | APRIL 2022 Spinning Light Wand Toy Adaptation user Quick Guide (for v1.0 printed base)

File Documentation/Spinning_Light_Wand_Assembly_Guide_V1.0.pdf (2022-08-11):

V1.0 | APRIL 2022

## Spinning Light Wand Toy Adaptation

## ASSEMBLY GUIDE (FOR V1.0 PRINTED BASE)

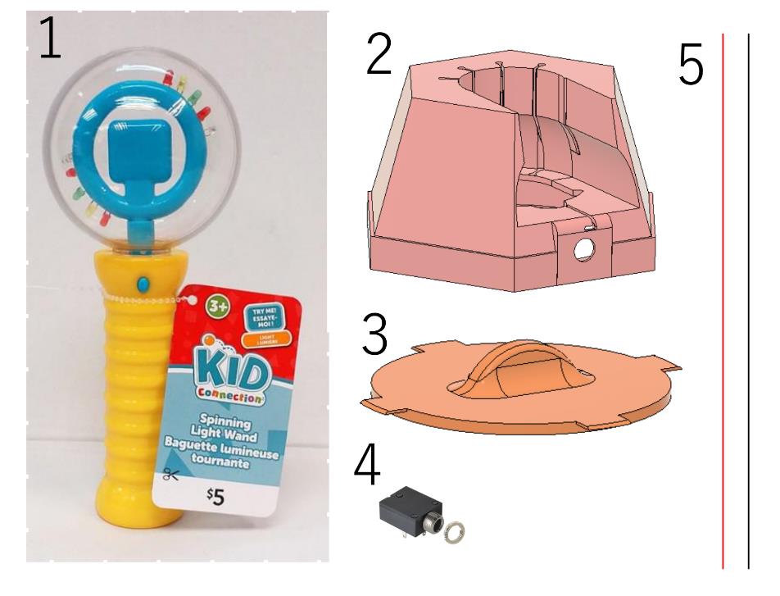
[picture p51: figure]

© 2022 by Neil Squire / Makers Making Change. Photos and text by Mimi Xia. This work is licensed under the CC BY NC SA 4.0 License: http://creativecommons.org/licenses/by-nc-sa/4.0
Files available at https://makersmakingchange.com/project/spinning-light-wand-toy-adaptation/ (https://makersmakingchange.com/?post_type=project&p=14500&preview=true) | Page 1 of 10

### Required Components

BOM
1. Spinning Wand Toy
2. 3D Printed Base
3. 3D Printed Base

Bottom Cover

4. 3.5 mm Mono jack
5. 2X 20 cm 26AWG

multi-core wire or

stranded wire (24-26

AWG)

### Required Tools

- #0 Phillips Screwdriver
- Flat head screwdriver
- Soldering Iron
- Hot Glue Gun
- Solder
- Hot Glue Sticks
- Super Glue

### Required Personal Protective Equipment (PPE)

- Safety Glasses

## ASSEMBLY GUIDE (FOR V1.0 PRINTED BASE)

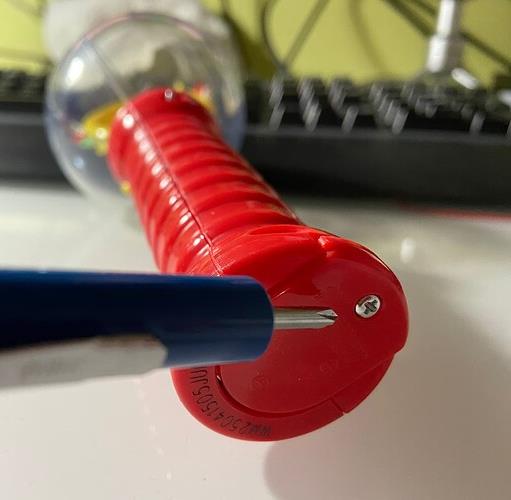
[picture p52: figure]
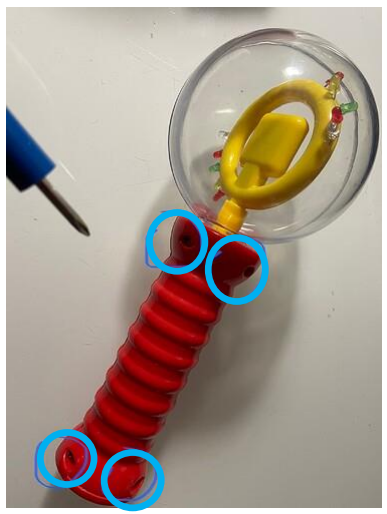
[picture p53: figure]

Files available at https://makersmakingchange.com/project/spinning-light-wand-toy-adaptation/ (https://makersmakingchange.com/?post_type=project&p=14500&preview=true) | Page 2 of 10

### Assembly Instructions

### Step 1

Loosen the screw and remove the battery cover and batteries.

CAUTION! The springs on the battery contacts may cause the batteries to be ejected forcibly.

### Step 2

Unscrew the four (4) screws on the back of the Spinning Light Wand. Store the screws for later reassembly.

CAUTION! Don’t lose the screws.

## ASSEMBLY GUIDE (FOR V1.0 PRINTED BASE)

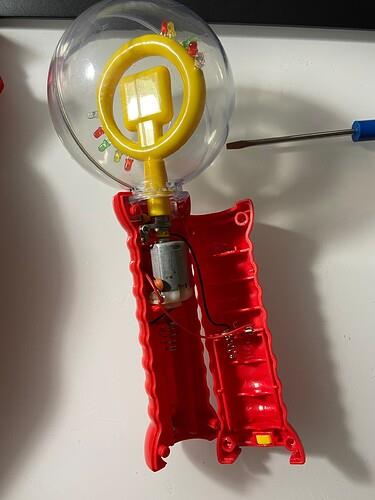
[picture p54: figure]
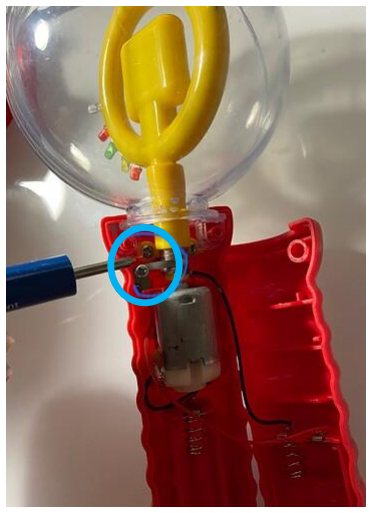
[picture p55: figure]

Files available at https://makersmakingchange.com/project/spinning-light-wand-toy-adaptation/ (https://makersmakingchange.com/?post_type=project&p=14500&preview=true) | Page 3 of 10

### Step 3

Gently pry apart the two halves of the handle along
the seam using a flat head screwdriver.

### Step 4

Remove the screw holding the motor down, as shown in the photo, and remove the piece of metal contact. Keep the screw for later reassembly.

CAUTION! Don’t lose the screw or the metal contact.

## ASSEMBLY GUIDE (FOR V1.0 PRINTED BASE)

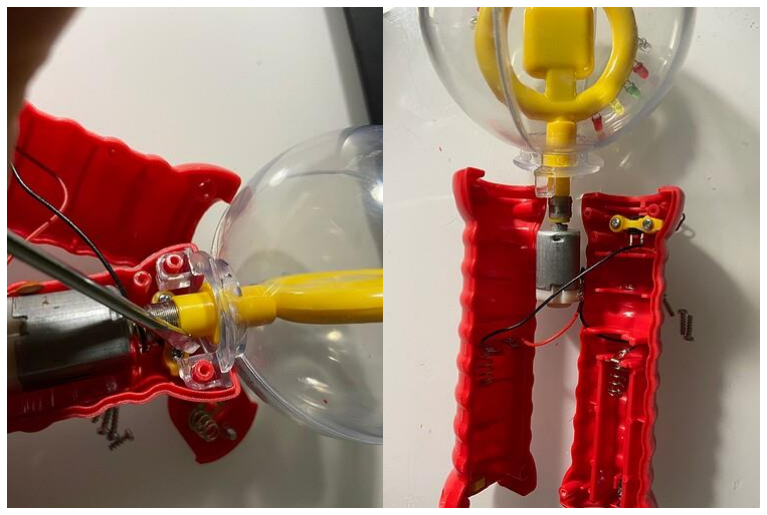
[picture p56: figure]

Files available at https://makersmakingchange.com/project/spinning-light-wand-toy-adaptation/ (https://makersmakingchange.com/?post_type=project&p=14500&preview=true) | Page 4 of 10

### Step 5

Gently pry the clear globe free from the button half of the handle The motor and the clear globe is part of the same assembly, carefully lay all the parts out, and try and avoid putting strain on any of the solder joints.

### Step 6

De-solder the black wire from the top of the battery holder and the red wire on the other half from the bottom of the battery holder. For the red wire, it may be easier to loosen the screw to remove the wire from under the metal clip.

## ASSEMBLY GUIDE (FOR V1.0 PRINTED BASE)


Files available at https://makersmakingchange.com/project/spinning-light-wand-toy-adaptation/ (https://makersmakingchange.com/?post_type=project&p=14500&preview=true) | Page 5 of 10

### Step 7

Unscrew the screws attached to the yellow piece shown. Remove and discard the entire button assembly. They are no longer needed.

### Step 8

Cut 2 pieces of wire 30cm long. Strip approximately 1cm of the insulation from one end of each of the wires.

### Step 9

Solder one of the wires to the bottom metal clip and route the wire as shown below. This is the same place where the original red wire was soldered.

## ASSEMBLY GUIDE (FOR V1.0 PRINTED BASE)


Files available at https://makersmakingchange.com/project/spinning-light-wand-toy-adaptation/ (https://makersmakingchange.com/?post_type=project&p=14500&preview=true) | Page 6 of 10

### Step 10

Solder the second wire to the battery clip. This is the same place that the original black wire was desoldered from.

### Step 11

Thread the wires through the hole that the button occupied. Avoid leaving too much slack on the wires inside as it might interfere with the moving bits.

### Step 12

Route the wires through the inside of the handle as shown.

## ASSEMBLY GUIDE (FOR V1.0 PRINTED BASE)


Files available at https://makersmakingchange.com/project/spinning-light-wand-toy-adaptation/ (https://makersmakingchange.com/?post_type=project&p=14500&preview=true) | Page 7 of 10

### Step 13

Apply hot glue to fill up space between the wire and the hole, to add strain relief to the wire.

### Step 14

Start reassembling the wand by putting the globe and motor assembly back into the half of the handle with the button hole. Note the alignment of the motor and the clear globe. See photos.

## ASSEMBLY GUIDE (FOR V1.0 PRINTED BASE)


Files available at https://makersmakingchange.com/project/spinning-light-wand-toy-adaptation/ (https://makersmakingchange.com/?post_type=project&p=14500&preview=true) | Page 8 of 10

### Step 15

Reattach the L-shaped metal contact. Replace the screw.

### Step 16

Snap the handle closed, being careful not to pinch any wires inside. Replace all four screws. Re-insert the batteries and tighten the battery cover screw.

### Step 17

Test the switch adaptation.
Strip the other end of the wire and touch them together. If all goes well, the motor should spin and the light would come on. If not, re-open the handle and check:

## ASSEMBLY GUIDE (FOR V1.0 PRINTED BASE)


Files available at https://makersmakingchange.com/project/spinning-light-wand-toy-adaptation/ (https://makersmakingchange.com/?post_type=project&p=14500&preview=true) | Page 9 of 10
- wiring: no cold solder joints or frayed/pinched wires
- mechanical interference: now wires are rubbing on the axle
- the L-shaped metal piece is making good contact against the spring on the motor axle.

### Step 18

Slide the wand into the stand. Make sure the battery cover is lined up with the opening in the stand.

### Step 19

Thread the wire through the opening of the stand. Solder the wires to a mono jack as shown in photo. The wires
should attach to the tip and sleeve contacts on the jack.

## ASSEMBLY GUIDE (FOR V1.0 PRINTED BASE)


Files available at https://makersmakingchange.com/project/spinning-light-wand-toy-adaptation/ (https://makersmakingchange.com/?post_type=project&p=14500&preview=true) | Page 10 of 10

### Step 20

Insert the jack into the hole in the base. Thread on the nut to secure the jack in place.

### Step 21

Superglue something heavy like two hex nuts to the Base Bottom Cover to weigh the stand down.

### Step 22

Assemble the base bottom cover into the base.

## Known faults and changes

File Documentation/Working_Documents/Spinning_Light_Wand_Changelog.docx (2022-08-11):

# Version 1.1 | Date 2022-June-17

- Updated 3D printed base to reduce print time and the need for print supports.
- CAD design by Jake McIvor – Makers Making Change.
- Updated the original documentation.

# Version 1.0 | Date 2020-April-13

- Initial version
- CAD design, assembly text and photos by Mimi Xia
- Documentation by Neil Squire / Makers Making Change.

© 2022 by Neil Squire / Makers Making Change. This work is licensed under the CC BY NC SA 4.0 License: http://creativecommons.org/licenses/by-nc-sa/4.0 Files available at https://makersmakingchange.com/project/spinning-light-wand-toy-adaptation/ Page 1 of 1

V1.1 | JUNE 2022 Spinning Light Wand Toy Adaptation changelog

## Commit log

2022-04-13 Add assembly photos
2022-04-13 Add CAD files
    [Spinning_Light_Wand_Adaptation.f3d]
2022-04-13 Add build files
    [Base.stl, Base_Bottom_Cover.stl]
2022-04-13 Add initial documentation.
    [Spinning_Light_Wand_Adaptation_BOM_V1.0.xlsx]
2022-04-13 Add 3d printing files
    [Base.stl, Base_Bottom_Cover.stl]
2022-04-21 Shorten filenames
    [Spinning_Light_Wand_Adaptation_BOM_V1.0.xlsx, Spinning_Light_Wand_BOM_V1.0.xlsx]
2022-04-21 Add versioned pdf documentation
    [Spinning_Light_Wand_BOM_V1.0.csv]
